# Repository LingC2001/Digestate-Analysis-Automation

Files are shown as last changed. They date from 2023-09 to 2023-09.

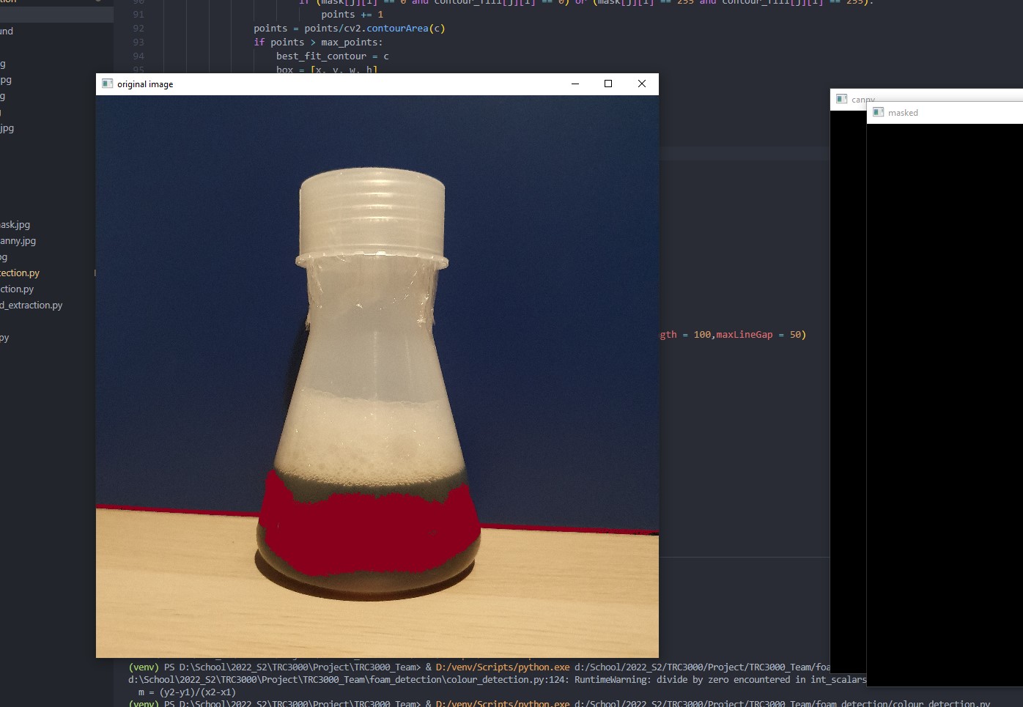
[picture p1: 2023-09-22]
foam_detection/images/noise_test.jpg

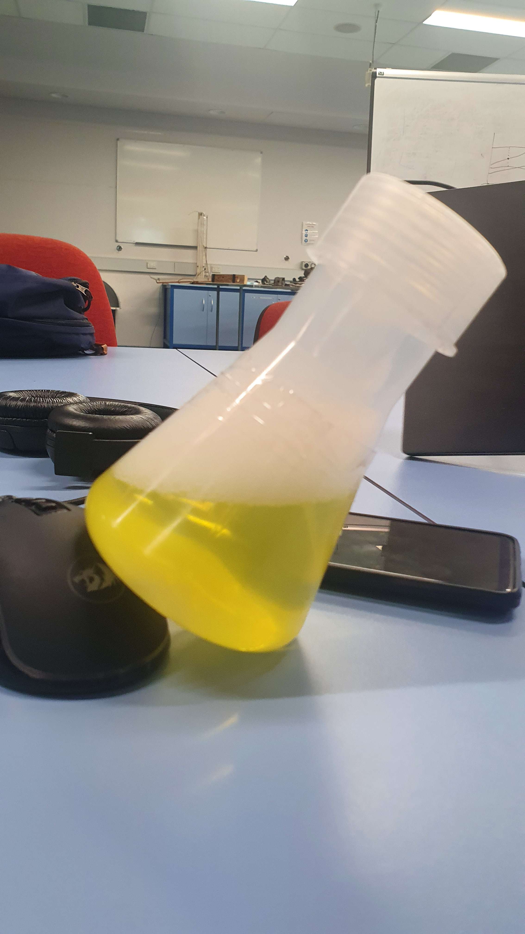
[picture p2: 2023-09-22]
foam_detection/images/test3.jpg

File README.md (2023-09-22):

# Digestate-Analysis-Automation
Development of an automated system for perfoming digestate analysis for anerobic tanks.

## Project Brief
In anaerobic digestion (AD), microorganisms are used to break down biodegradable material in the absence of oxygen. The process helps to solve two major problems in the world today. Firstly, it helps to to treat the biodegradable waste and sewage sludge that are produced in ever increasing amounts each year. Secondly, AD may be used as a source of renewable energy.
However, foaming poses an operational problem in anaerobic digesters. 

Project Objectives:
- Conduct operational interfacing of an anaerobic digester sample tester experimentation kit.
- Design a commercial ready portable anaerobic digester sample tester.

## Description
An machine learning approach was taken. Sample tester contains cameras, servos, load cells and temperature sensors to perform full analysis of digestate.

Design
Device
Foam Detection

### Built With
- 
- 
- 

## Authors
- Ling Chen, LingC2001@gmail.com | lche0147@student.monash.edu
- John Nguyen
- Xavier Andueza
- Kabir Chugh
- Jason Ltg
- Ritchie Leong

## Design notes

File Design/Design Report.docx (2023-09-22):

# Team232 Project Design

Part A: Supplementary information document

Xavier Andueza,

Ritchie Leong,

Ling Chen,

Kabir Chugh,

Jason Ung,

John,

# Executive Summary

Do after everything else has been written up.

Contents

1.0 Executive Summary 2

Contents 3

2.0 Introduction 4

3.0 Proof of Concept 5

3.1 Foam Detection Algorithm Summary 5

3.1.1 Background Removal 5

3.1.2 Bounding Box 5

3.1.3 Foam Detection Network 5

3.1.4 Information Extraction 5

4.0 Final Product Design 5

4.1 Expected End-Use Environment 5

4.2 Design Requirements 6

4.2.1 Hard Design Requirements 6

4.2.2 Soft Design Requirements 6

4.3 Overview of Final Product Design 7

4.4 Sub-assembly Analysis 7

5.0 Costings 7

# Introduction

Team 232’s innovative design is to be used for testing and diagnosis of digestate from an anaerobic digester (AD). It is intended to be portable, and carried around so that it can be screwed digestate release valves at customer sites.

The design is broken into three main sub-assemblies (SAs), being the:

- Hard plastic chassis, handle and rubber grip;
- Digestate container; and
- Electricals.

In creating the design, Team 232 has considered several hard and soft design requirements. The ways in which the requirements are met by the design are explored in this supplementary report. A part and purchase part list, with anticipated costs, notes and remarks are also included.

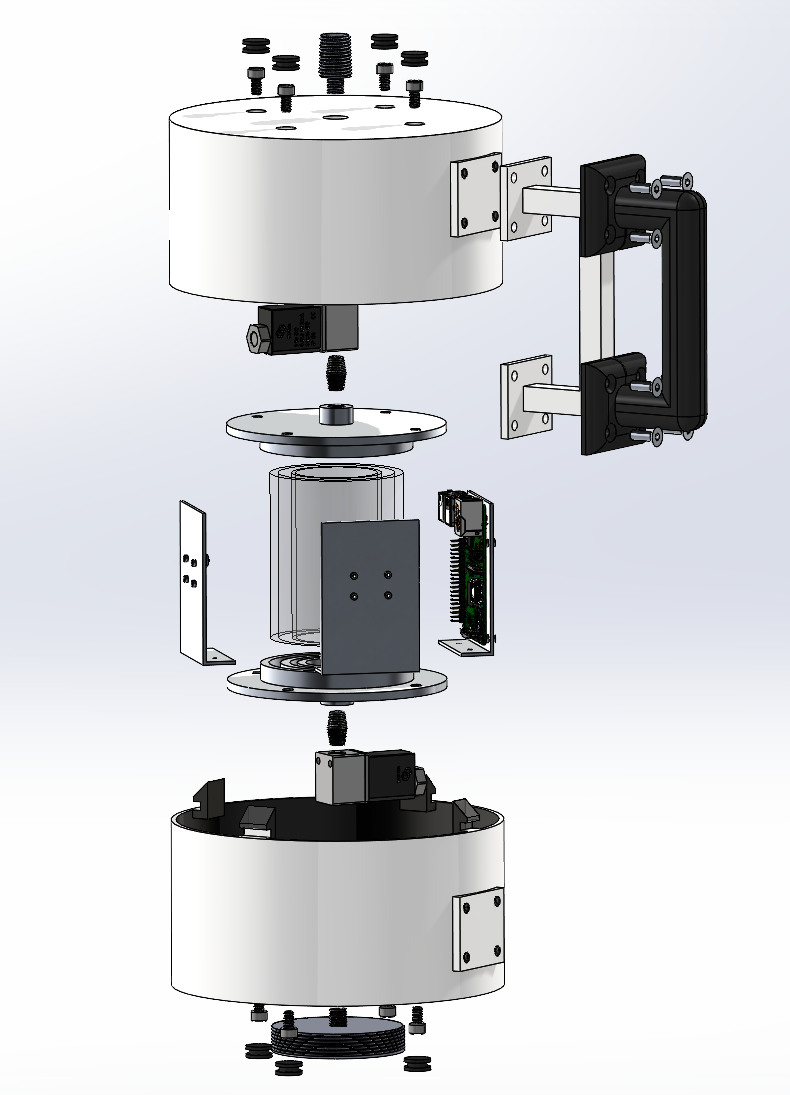
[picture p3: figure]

Figure 4.3.1: Expanded Mechanical Components View

# List of Design Requirements

All requirements were procured through market research performed by Monash University.

## Hard Requirements

The “Hard Requirements” are defined as the requirements that must be included in the design, and the design is considered insufficient without these.

Requirement | Specification
Hold digestate for analysis | ≥100mL
Dry weight (no digestate) | <10kg
Instrument base area | <0.08m^2
Hold electronics internally | -
Battery operated | -
Carry-friendly | -
No sharp corners | -

## Soft Requirements

The “Soft Requirements” can be considered to be the factors that are considered by the target audience when making a purchase decision, but are typically not deal breakers to them. Team 232 assigned weighting factors to the Soft Requirements to establish a hierarchy of importance. This enabled the team to make better decisions when maximising one factor may come at the expense of another.

Requirement | Aim | Weighting Factor
Cost | Minimise | 5
Weight | Minimise | 9
Height | Minimise, but ensure comfortable handling | 8
Surface Area | Minimise, but ensure comfortable handling | 8
Aesthetics | Aesthetically appealing | 3
Servicing Difficulty | Minimise | 5
Amount of metal parts | Minimise | 5
Manufacturing difficulty | Minimise | 5

# SA1: Hard Plastic Chassis, Handle and Rubber Grip Sub-Assembly

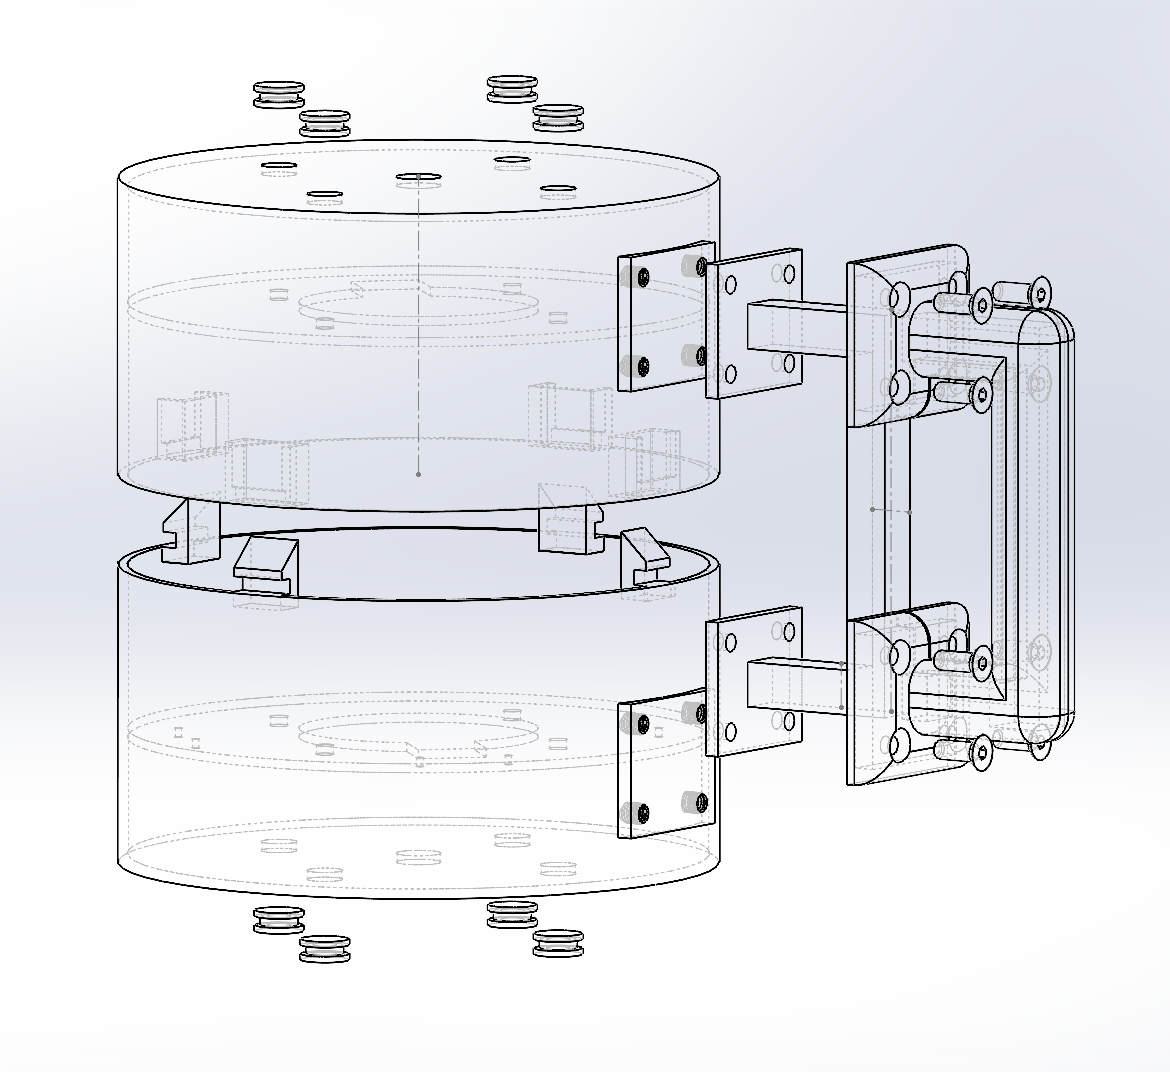
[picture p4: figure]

Figure X: AAA

## 4.1 Sub-Assembly Part List

Insert the part list

## 4.1 Hard Requirements Satisfied

Insert table and explanations

## 4.1 Soft Requirement Maximisation

Insert table and explanations

# SA2: Digestate Container

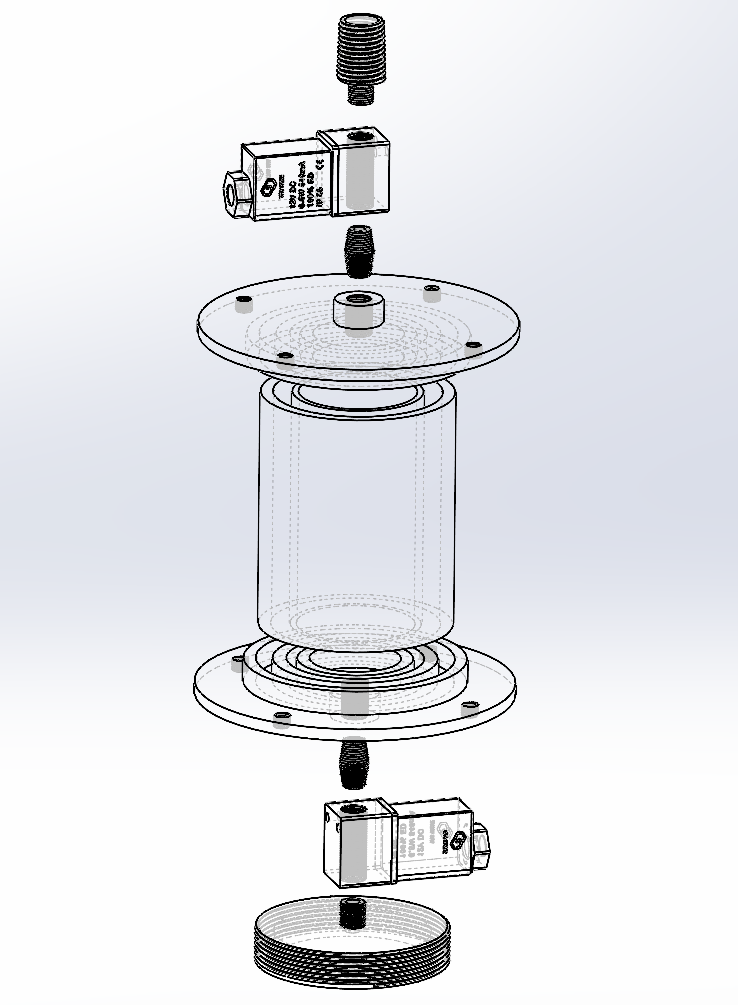
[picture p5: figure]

Figure X: AAA

## 4.1 Sub-Assembly Part List

Insert the part list

## 4.1 Hard Requirements Satisfied

Insert table and explanations

## 4.1 Soft Requirement Maximisation

Insert table and explanations

# SA3: Electricals

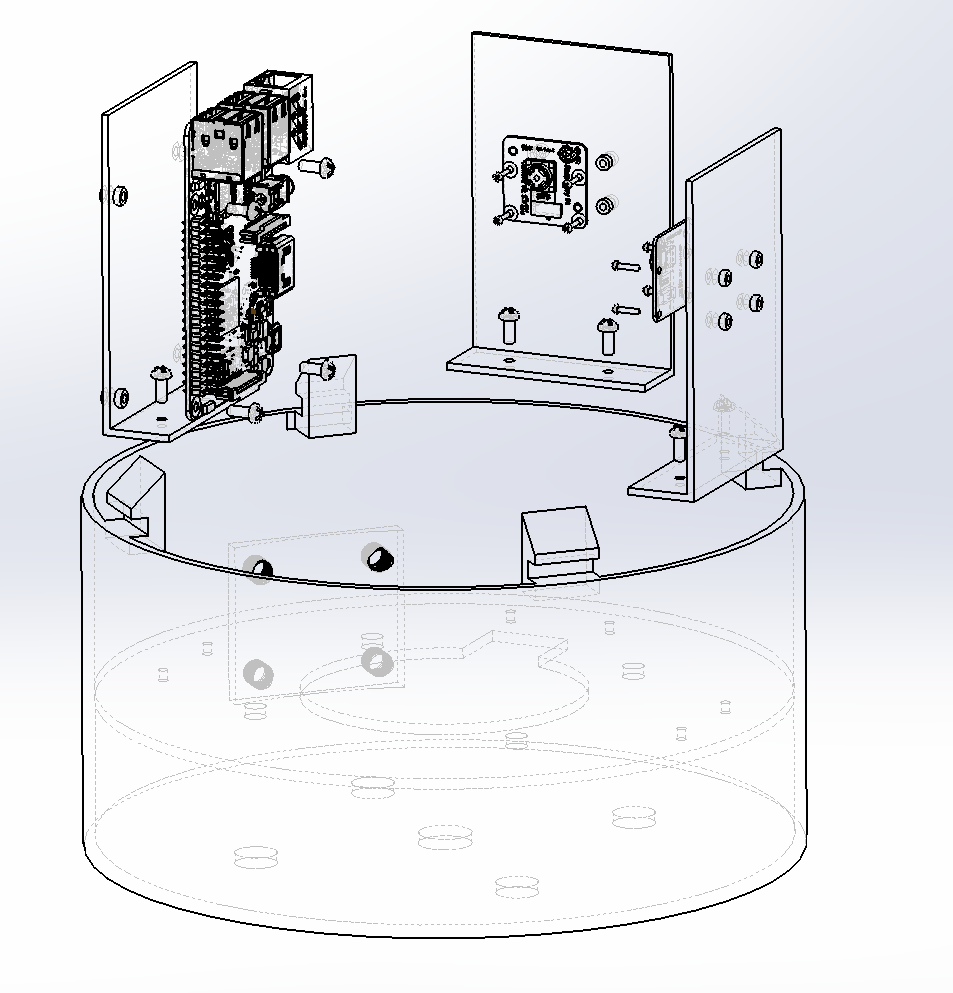
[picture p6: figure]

Figure X: AAA

## 4.1 Sub-Assembly Part List

Insert the part list

## 4.1 Hard Requirements Satisfied

Insert table and explanations

## 4.1 Soft Requirement Maximisation

Insert table and explanations

# 4.0 Final Product Design

## 4.1 Expected End-Use Environment

T232’s instrument's target audience is organisations that use ADs. These ADs will generally always be outside, and therefore the instrument will be exposed to a broad range of climates. The unit will be portable and will be taken closer to the ADs so that testing can be conducted. The unit may be transported and left in vehicles, which may expose the unit to even higher temperatures than the outside climate. Furthermore, T232’s Instrument may also experience significant shocks and vibrations at the customer sites, as users may accidentally drop the unit, or otherwise leave it unsecured in a vehicle as it travels bumpy roads. It is not anticipated that T232’s Instrument will be exposed to particularly detrimental electric shocks or electromagnetic interference.

Expected environments for the unit were defined as so:

Table 4.1: Expected end-use environmental conditions

Specification Type | Operational | Survival
Temperature | 0°C - 40°C | -20°C - 60°C
Humidity | 20-80% RH | 10-100% RH
Shock
Vibration

## 4.2 Design Requirements

Design requirements were established by engaging with the target audience and understanding their perspective, as well as an analysis of the conditions in the end-use environment. They were broken down into Hard Specifications (the “must-haves”) and Soft Specifications (which are maximised against).

### 4.2.1 Hard Design Requirements

Table 4.2.1: Hard Design Requirements

Requirement | Specification
Hold digestate for analysis | ≥100mL
Dry weight (no digestate) | <10kg
Instrument base area | <0.08m^2
Hold electronics internally | -
Battery operated | -
Carry-friendly | -
No sharp corners | -

### 4.2.2 Soft Design Requirements

Soft requirements were interpreted through a weighting factor. The higher the weighting factor the greater the design should factor this in.

Table 4.2.2: Soft Design Requirements

Requirement | Aim | Weighting Factor
Cost | Minimise | 5
Weight | Minimise | 9
Height | Minimise, but ensure comfortable handling | 8
Surface Area | Minimise, but ensure comfortable handling | 8
Aesthetics | Aesthetically appealing | 3
Servicing Difficulty | Minimise | 5
Amount of metal parts | Minimise | 5
Manufacturing difficulty | Minimise | 5

## 4.4 Sub-assembly Analysis

- Break things down into the individual sub-components. Explain the design decisions that were made, what they maximised and how assembly will work. Give details to dimensions:
  - Fluid compartment sub-assembly
    - Expanded assembly view
    - Details of components, how they would be manufactured
    - Details of joiner (Araldite Temperature Cured solution)
  - Outer shell
    - Expanded view
    - Highlight intended manufacturing method, plastic molds
    - Highlight clipping (and how it can only clip in the one way)
    - Highlight how grip is secured
  - Electronics
    - Image of electronics secured down
    - Highlight how, where they are secured

# 5.0 Costings

Provide reasonable costings breakdown

Table 5.1: Costing Summary

Parts | Quantity | Cost ($) per unit | Source

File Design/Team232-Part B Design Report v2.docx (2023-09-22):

# Part B Design Report Team232

Xavier Andueza,

Ritchie Leong,

Ling Chen,

Kabir Chugh,

Jason Ung,

John Nguyen

# 1. Design Features

## 1.1 Handle/Grip

One of the main features in our design is the handle. The handle allows the device to be carried around by the user. When held by the user, the handle is the most critical part supporting the weight of the whole device. Thus, we have analysed the handle by running FEA simulations to find the stresses and displacement of the handle.

# 2. Calculations and Assumptions

## 2.1 Mass of the device

### 2.1.1 Mass of components

- Tester device (derived from Solidworks) without the 10mm solenoid valve, Pi camera, Raspberry Pi 4, White LED strips, and battery is 2964.87g
- Two 10mm solenoid valve is 4.5g X 2 = 9g
- Two Pi camera is 3g X 2 = 6g
- Raspberry Pi is 46g
- 0.05m LED strips (3 LEDs) is 350g÷100=3.5g
- Battery is 57g

Total mass of the device is 2964.87g+9g++6g+46g+3.5g+57g=3086.37g

We analyse for the system at full volume of Anaerobic Digestate.

### 2.1.2 Size of the flask

The inner glass tube has an inner diameter 5cm (radius 2.5 cm) and height 10cm

The volume of the flask =πr^2 h=π×2.5^2 ×10=196.3cm^3

### 2.1.3 Mass of Anaerobic Digestate (AD)

The density of AD is approximately 1 g/cm^3

The maximum amount of AD allowed in the system is 196.3cm^3 ×1g/cm^3 =196.3g

## 2.2 Weight of the device

When the glass is fully filled with AD, the total weight of the device is

F_(Total) =((3086.37g+196.3g))/1000×(9.81m)/(s^2)=32.2N

## 2.3 Servomotor and Rotating platform

## 2.3.1 Turning speed of rotating platform

The servomotor rotates at a max operational speed and has a maximum range of 180°. To calculate the angular velocity in units of rad/s is as follows, where θ is how range of rotation in degrees, and t is time to reach said rotational angle in seconds.

Rotational speed ((rad)/s) = θ/t ×π/180

## 2.3.2 Angular control

From the gpiozero library, provided code details how the servomotor rotates. “servo.min()” rotates the servo to starting position or 0°. “servo.mid()” rotates to 90° or midway and “servo.max()” rotates to end position or 180°.

Another way to control the position of the servo is by setting the value of the servomotor using the line of code: “servo.value = x”, where x is a real number between –1(min) and 1(max). This implies that a value of –1 corresponds to 0°, 0 corresponds to 90° and 1 corresponds to 180°. From this a function was created whereby a user enters a value between 0° and 180°. θ is in angle of rotation in units of degrees.

Value = cos(θ) ×-1

However, because in Python, a math library is required to access these tools, the function is more accurately as follows:

servo.value = math.cos(math.radians(θ)) ×-1

# 3. Simulations

## 3.1 Handle/Grip

The weight (32.2N) of the device acting on the handle is used in the FEA simulation to find the stresses and displacement of the handle.

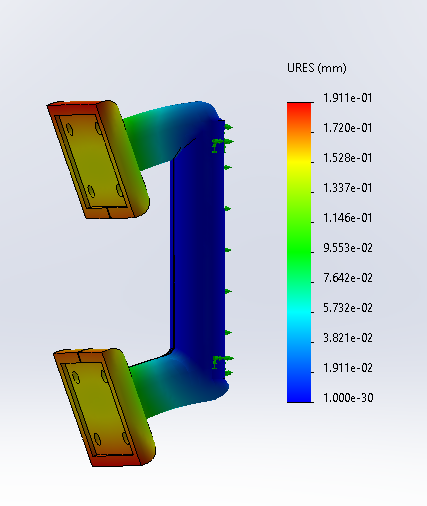
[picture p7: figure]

Figure 1: FEA displacement of handle and grip

Through FEA simulation, the max displacement of the handle (shown in Figure 1) is on the rubber grip. The max displacement is approximately 0.19mm, which is acceptable since the material is rubber. The max displacement on the plastic (ABS) handle itself is around 0.15mm and is negligible.

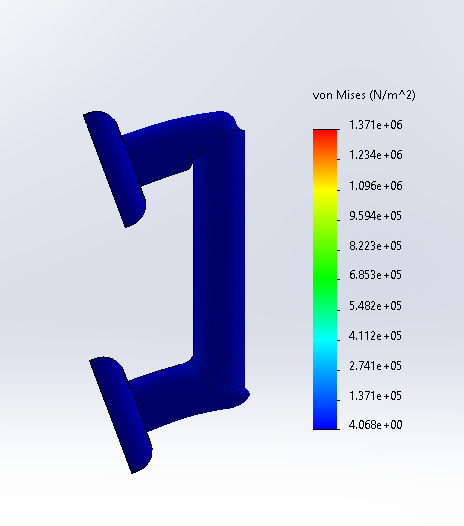
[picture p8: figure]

Figure 2: FEA stress of handle and grip

Through FEA simulation, the max stress (shown in Figure 2) experienced by the plastic handle is approximately 1.37MPa. The maximum allowed stress for ABS is 315MPa. So, the safety factor of the handle design is 230. Thus, we are very confident that the handle design will not fail, it is very safe.

# 4. Physical Experiments

## 4.1. Camera Testing

The proposed design of our device heavily relies on the reliability of the camera image analysis. It is the core functionality of the device and is crucial to the successful extraction of anerobic digestate information. The thorough tests in the following sub-sections are done to help determine and justify key design features needed to assist the functionality of the image analysis algorithm.

### 4.1.1. Background Removal Testing

Background removal is the first step needed in the analysis process; hence it is crucial to ensure successful background removal. The following Figure X

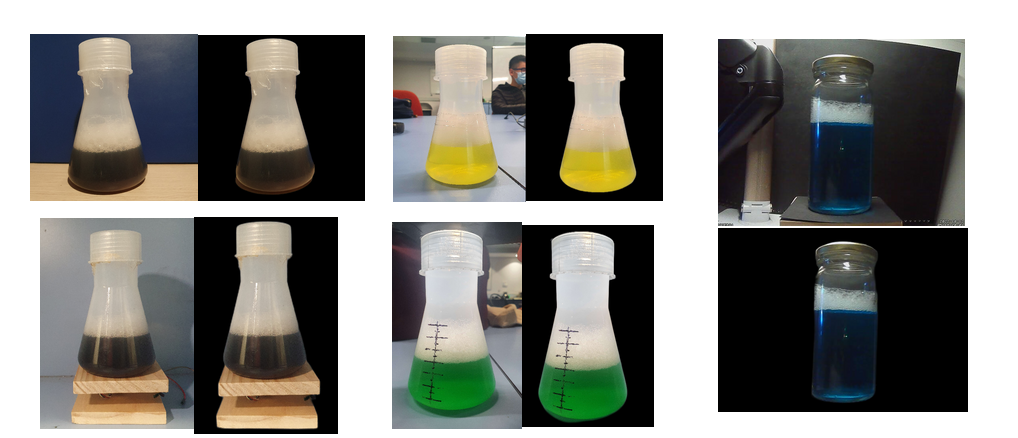
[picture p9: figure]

Figure 3:Background removal tests

As seen from Figure X, the background can be successfully removed in most environments, however there are still some cases where the useless and interfering objects remain in the image after removal. Therefore, to combat this problem in the design, we ensure that the glass tube containing the flask is completely sealed by an outer casing where the inside is painted black. This would completely remove the chance of unwanted background interference.

Furthermore, the background removal AI (Artificial Intelligence) is designed in a way where ideally the object of interest should be somewhere in the middle of the camera frame. In this design this is accounted for by keeping the anerobic digestate in a central glass tube and having the cameras pointed directly at it.

### 4.1.2. Image Resolution Testing

The image resolution test was done to determine the minimum required camera resolution that was needed to achieve accurate extraction of key information in the image. Using this information an appropriate camera suited for the purpose can be selected. Another small consideration was the running time of the code. The testing results are shown in Figure X below.

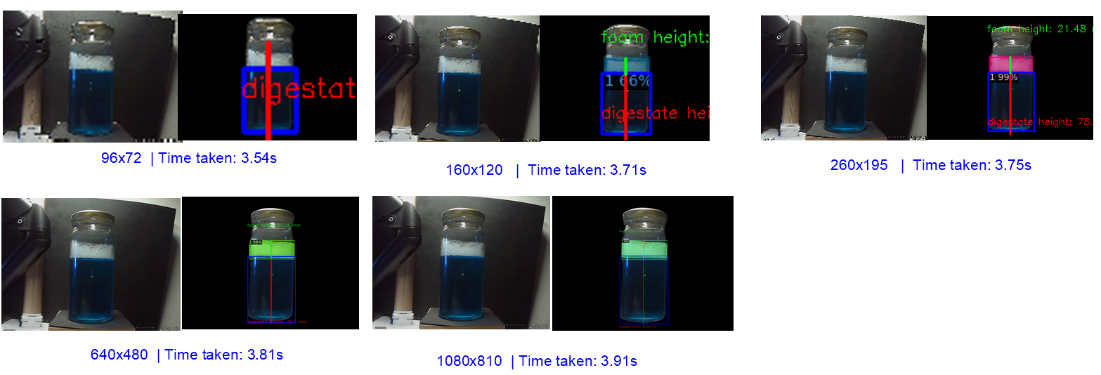
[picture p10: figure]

Figure 4:Camera resolution tests

Several conclusions can be drawn from the above Figure. Firstly, the tests demonstrate that foam and digestate regions can be accurately detected even with small resolution of 160x120, however it fails at resolutions below that due to too much loss of information. Another thing is that the lower the resolution, the more error the height measurements will be, as there are simply less pixels hence much larger height increments.

Another observation is that the running time of python scripts are similar despite the increase of resolution. This is due to the running time being primarily dominated by the loading of the neural network model weights. However, this test was done on a computer much more powerful than the raspberry pi, hence the actual running time may be longer.

Taking all of these into account, it was determined that 640x480 resolution is the best suited resolution that would reliably work with the algorithm without the loss of too much information. This also allows the design to be suited with a cheaper and lighter camera.

### 4.1.3. Algorithm Detection Robustness and Accuracy

To ensure that the detection algorithm is robust and accurate enough to use on digestate and foam of any colour and amount, thorough testing has been conducted on simulated samples of different colours and amounts. The figure below shows some tests done:

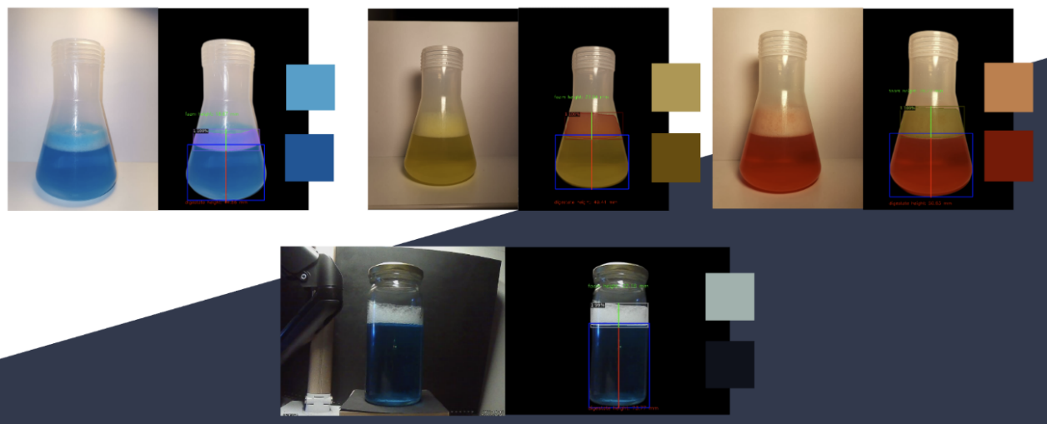
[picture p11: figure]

Figure 5: Varying Colour Tests

The results of these tests are summarised in the table below:

Table 1: Error Table

Test Sample | Detected Foam Height (mm) | Actual Foam Height (mm) | %Error | Detected Digestate Height (mm) | Actual Digestate Height (mm) | %Error
Light Blue | Less Foam | 19.31 | 17 | 13.59 | 42.26 | 42 | 0.62
Light Blue | More Foam | 25.61 | 25 | 2.44 | 48.92 | 46 | 6.35
Black | Less Foam | 20.39 | 19 | 7.32 | 44.12 | 43 | 2.60
Black| More Foam | 29.4 | 27 | 8.89 | 45.56 | 44 | 3.55
Green | Less Foam | 18.99 | 19 | 0.05 | 51.96 | 50 | 3.92
Green | More Foam | 28.92 | 29 | 0.28 | 50.06 | 48 | 4.29
Red | Less Foam | 19.23 | 17 | 13.12 | 48.44 | 46 | 5.30
Red | More Foam | 26.93 | 27 | 0.26 | 51.79 | 50 | 3.58
Yellow | Less Foam | 16.66 | 16 | 4.13 | 50.22 | 50 | 0.44
Yellow | More Foam | 26.32 | 26 | 1.23 | 50.25 | 50 | 0.50
Orange | Less Foam | 17.74 | 17 | 4.35 | 51.55 | 50 | 3.10
Orange | More Foam | 25.3 | 24 | 5.42 | 51.09 | 50 | 2.18
Average: | | | 5.09 % | | | 3.04%

As seen from the results above, the average error is around 3-5% which is acceptable for our design, however there were some images where error went as high as 13%. These cases of higher error are due to incorrect camera angles. When the camera angle is not directly perpendicular to the foam level line, it causes the side of the foam to appear taller in the camera than the centre of the foam, which causes errors in the foam bounding box detection. Another issue is the parallax error.

To minimise this, in the design the camera is placed directly facing the centre of the glass tube, and the amount of digestate in the device required for analysis will be consistent, hence the camera will always be pointed at the foam level, which helps to minimise the errors discussed above.

## 4.2 Servomotor Testing

## 4.2.1 Range of rotation

There exist many types of servomotors, which are characterized by their rotational behaviour. A continuous rotation servo is a servomotor that can rotate continuously in either direction for as long as the user desires. Speed of rotating and time rotating can be controlled. A linear servo is a servomotor that does not rotate but moves back and forth like a rack and pinon system. A positional rotation servo is a servomotor that is limited a range of roughly 180°. Only the position of the servo can be controlled. The positional rotation type servomotor was utilized in this project.

The gpiozero library was employed to allow rotational control of the servo. The minimum pulse width and maximum pulse width values are essential in determining the maximum range of rotation. Within the data sheet of servomotors contains the standard minimum and maximum pulse width values. However, as all servomotors are not built the same, these values are merely suggestions, and the true bounds of the range of rotation must be experimentally determined. It was found that at a minimum pulse width value of 0.5 milliseconds and a maximum pulse value of 2.33/1000 seconds satisfies the bounds of 180° rotation.

## 4.2.2 Varying speed and varying load

By varying the speeds and the load on the platform, we can identify patterns that could not have been clearly identified.

Modes of speed include - Slow, medium, fast and max speed.
Weight of loads include - No load, 100ml filled flask, 200ml filled flask and 300ml filled flask.

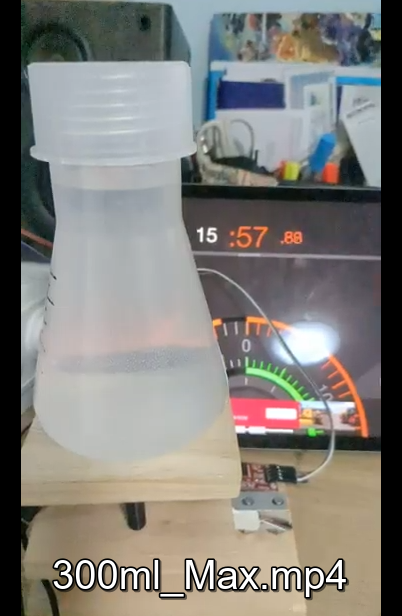
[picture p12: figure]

Figure 6: Flask with water on load cell

By placing a timer in the background, where its format includes milliseconds, we can use a x8 slow motion camera to measure the time taken to rotate to a specific angle. Through thorough testing and frame-by-frame analysis, we have obtained many samples and identified many relationships.

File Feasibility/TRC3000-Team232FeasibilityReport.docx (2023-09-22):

# Team232 Feasibility Report

Xavier Andueza,

Ritchie Leong,

Ling Chen,

Kabir Chugh,

Jason Ung,

John Nguyen

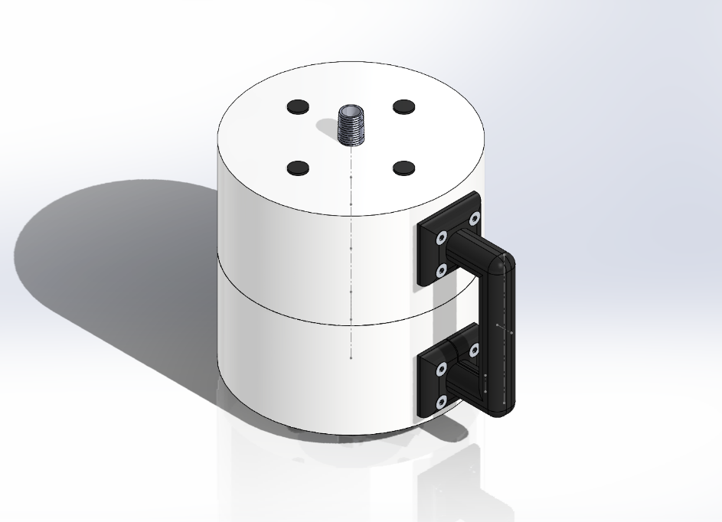
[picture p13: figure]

# 1.0 Executive Summary

Anaerobic Digestion (AD) in bioreactors can be significantly affected by the quality of the digestate contained within. Indicators of poor digestate quality include colour, and foaming. Testing of digestate quality is typically done by removing digestate from the container in an intermediate container, and then placing this digestate into a testing unit.

Team 232 (T232) has proposed an innovative new design that will disrupt this process, where the testing unit will plug directly into bioreactor release valves, immediately testing the digestate. In this feasibility report, the design is presented, and the three design sub-assemblies are justified, including estimated costs. Design decisions, including the material selection choices, are highlighted and explained. Visuals are presented to assist the reader in understanding how these sub-assemblies are assembled.

# 2 Introduction

In this report, the financial feasibility of the Team 232’s (T232’s) product is assessed. Justifications are made for the design decisions made, and costings are presented. References are made to the Bill of Material, which can be found accompanying this report.

## 2.1 Problem Statement

Anaerobic Digesters (AD) have been traditionally used in waste treatment to breakdown biodegradable waste and sewage sludge. It is also a source of renewable energy. However, the chemical processes can lead to a reduction in efficiency. This is indicated by foaming and a colour change in the digestate. Periodic testing of digestate must be performed, where the amount of foam and the foam colour is analysed. Intervention can occur if needed after analysing the digestate foam and colour.

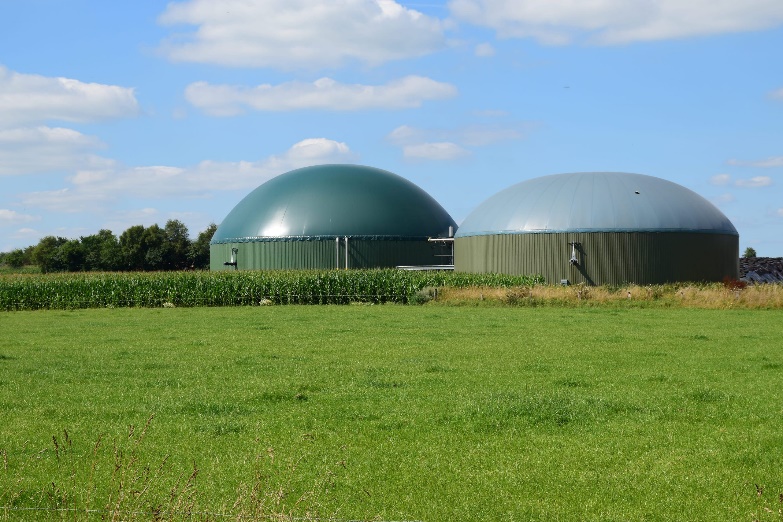
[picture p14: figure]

Figure 1: Anaerobic Digester plant

https://www.fgsorganics.co.uk/wp-content/uploads/2022/07/shutterstock_304576766-1-scaled.jpg

## 2.2 Proposed Solution

To enable better testing of ADs, Team 232 conducted successful proof-of-concept testing and has developed a proposed AD tester design, dubbed “T232’s Instrument”. T232’s Instrument enables rapid testing and diagnosis of digestate. The AD tester device allows users to extract a sample of the digestate from the AD tank and analyse digestate foam level and colour.

# 3 Design Summary

Figure 2: Image of the proposed final design of T232’s Instrument

T232’s Instrument can be broken down into three main sub-assemblies:

- The Chassis The hard plastic outer container that features the grip and contains the Fluid Compartment and Electronics within.
- The Digestate Container The metal and glass that contains the digestate during testing.
- The Electronics The circuits and other electrical components that enable analysis and diagnosis within the instrument.

These Sub-assemblies are broken down in their own segments, costings discussed, and design decisions justified.

## The Intention of the Design

To frame the design decisions made, the overall intended use of T232’s instrument will be explained.

Unlike other competitor products, where the digestate is brought to the instrument, T232’s is unique in that the instrument is brought to the unit. This is enabled through the design being such that the instrument is screwed into bioreactor fluid release valves. The digestate can then enter the body and be tested immediately.

# 4 The Chassis

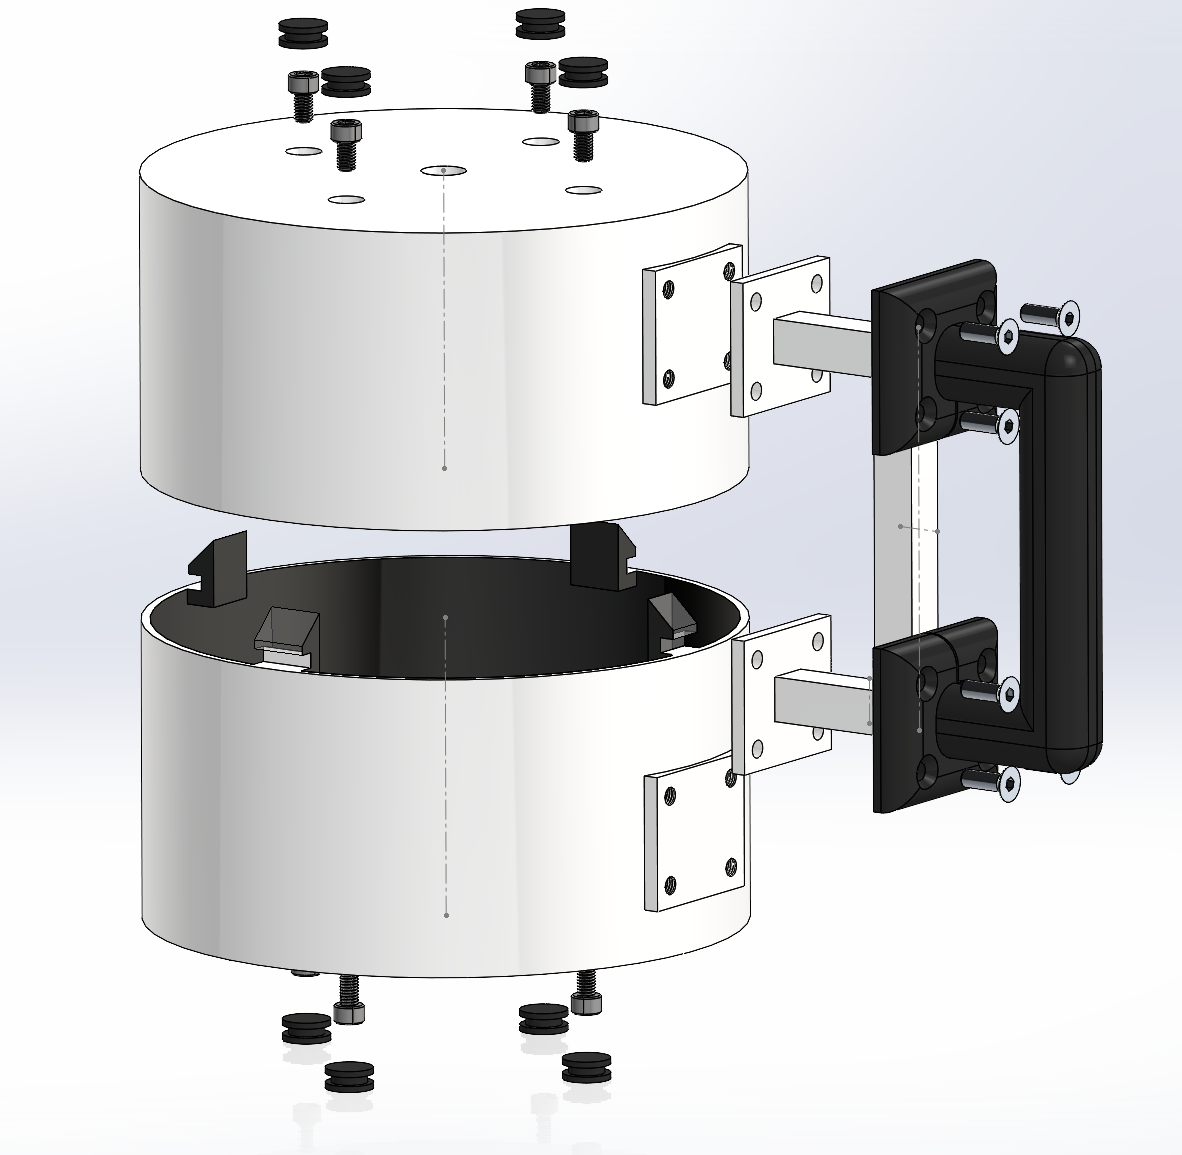
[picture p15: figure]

Figure 3: Disassembled view of T232’s Instrument’s Chassis

Table 1: Design justifications for the chassis

Name | Material | Cost ($) | Qty | Justification

Top Shell

Hard Plastic

58.55

x1

The top shell was decided to be made using a hard plastic, that is injection moulded. Hard plastic was deemed to be the most appropriate as it was a high priority for the design to be lightweight, but sturdy. Making the entire instrument out of Aluminium was considered, however it was deemed as being both too costly and heavy compared to the hard plastic.

The Top shell features four clip holes, which the bottom shell clips into for easy assembly. One of the clips is smaller than the others, meaning that there is only one way to assemble these two together, as it will not fit in any other way. This ensures that the handle holes in the top shell are aligned. It is a simple method that ensures that the manufacturing process is simple, yet able to ensure fewer mistakes are made.

Both the top and bottom shell feature holes for the 10mm M6 HEX heads to pass through, securing the Digestate Compartment to the Chassis. To enable the large solenoids to enter the bottom sections, there is a large opening for them.

Both the top and bottom shell have their inside painted black so that the images easily have the foam and background distinguished.
Bottom Shell | Hard Plastic | 58.51 | x1 | The Bottom shell features the bottom clips, that clip into the top shell clip shells.
10mm M6 HEX Bolt | Steel | 4.96 | x8 | These 10mm M6 HEX screws were chosen as they allow a large amount of torque to be applied. These secure the Digestate Compartment to the chassis. The top and bottom shell have holes, which allow the bolts to be screwed in through. HEX heads have an advantage of being resistant to threading, which, due to large torques being applied to ensure that the chassis and the fluid compartment, is a risk for other heads.
Rubber Nibs | Rubber | 8.00 | x8 | The rubber caps are placed onto the screw holes that exist in the chassis, and were chosen as rubber material is already being used on the grip, and to strengthen the black-on-white aesthetic of the instrument.
Handle | Hard Plastic | 21.38 | x1 | The handle is made of hard plastic, which is strong yet lightweight. As a rubber grip is placed on top of this, costs were reduced by making the grip square. This part is simple to injection mould, and will be quite cheap. Metals would be more expensive and weigh more.
Grip | Rubber | 33.87 | x1 | The Grip was selected to be a custom rubber grip, which is screwed into the handle and chassis through the 18mm countersunk M6 HEX Screws. Rubber grips are commonplace, and are comfortable to many consumers. A softer rubber allowed the handle design to be simpler, further reducing costs.
18mm countersunk M6 HEX Bolt | Steel | 8.70 | x8 | These 18mm countersunk M6 HEX screws are used to secure the grip and handle together, and into the chassis. These are utilised in place of the 10mm M6 HEX due to their need to be countersunk and the overall hole length being greater. Countersunk screws were chosen as these screws were customer facing, and having bulkier HEX heads resulted in a significantly loss of visual appeal to the customer, as screws were jutting out from the grip, which most customers associate with being smooth.

# 5 The Fluid Container

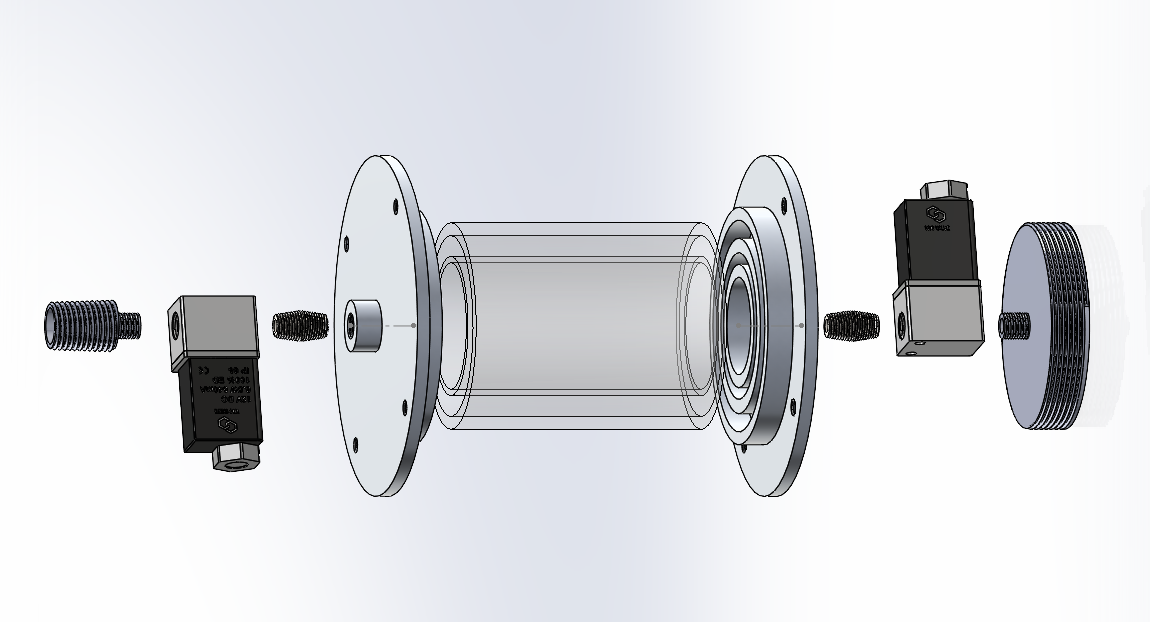
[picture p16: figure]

Figure 4: Disassembled view of the Digestate Container (flipped horizontally)

Table 2: Design justifications for the Digestate Container

Name | Material | Cost ($) | Qty | Justification
Valve connector | Stainless Steel Alloy | 66.00 | 1 | This valve connector was initially designed as a 20mm NPT head; however, it is extremely customisable to customer site needs. It was not worthwhile investigating off-the-shelf components due to the likely amount of variation from one customer site to another. A stainless-steel alloy was chosen for this part as the digestate, although anaerobic, may induce some rusting effects over time as air enters when outside of testing environments.
10mm 24V DC Solenoid Valve | NA | 99.00 | 2 | The solenoid valves are crucial to the intended purpose of the system. These valves control the flows in and out of the instrument and are highly precise. The valves are controlled via feedback from the raspberry Pi and will fill the glass vial up to the measurement point. These specific valves were chosen due to their smaller size, and appropriate valve opening widths.
Male-to-Male 10mm NPT connector | Stainless Steel Alloy | 98.00 | 2 | An NPT male-to-male connector was used as it ensures that there is extremely low chance of leakage, and also is a very simple way of connecting the solenoid valves to the tube plates.
Tube plates | Aluminium Alloy | 165.00 | 2 | The tube plates are custom made, and feature two sections for the glass tubes to be inserted into. Glass tubes are secured to the plates with adhesive. An aluminium alloy was selected due to the thicker nature of these components, and how the mass would make the unit less transportable and place greater strain on the glass tubes. The part is as thick as it is as this is where the digestate container is secured to the chassis with the 10mm M6 HEX bolts.

54mm wide, 2.5mm thick, 100mm tall tube

Glass

32.24

1

Glass was chosen as it is inert and allows for light to pass through for measurement purposes.

The dimensions of this were chosen as it enabled the digestate container to hold 100ml of fluid halfway up the glass vial, which was deemed the optimal camera location. The glass thickness was selected as this was the most representative of world-proven double-glazed glass.

This is also standard glass tubing that can be easily and cheaply ordered from many suppliers.

By providing insulation in this manner, the unit does not require heating elements to keep the digestate in its mesophilic state during testing. This significantly reduces design complexity and costs.
80mm wide, 5mm thick, 100mm tall tube | Glass | 3.95 | 1 | These dimensions were chosen as they enabled the standard double-glazed glass air gap between the two glass tubes. They are also slightly thicker than the standard outer-glass size, ensuring extra robustness from shocks and vibrations. This is also standard glass tubing that can be easily and cheaply ordered from many suppliers.
Bottom attachment | Aluminium Alloy | 54.00 | 1 | The aluminium alloy was selected as this is also one of the thickest parts and adds significant weight to the build. Stainless steel was deemed too heavy. This is a custom part and will be constant across all builds.

# 6 The Electronics

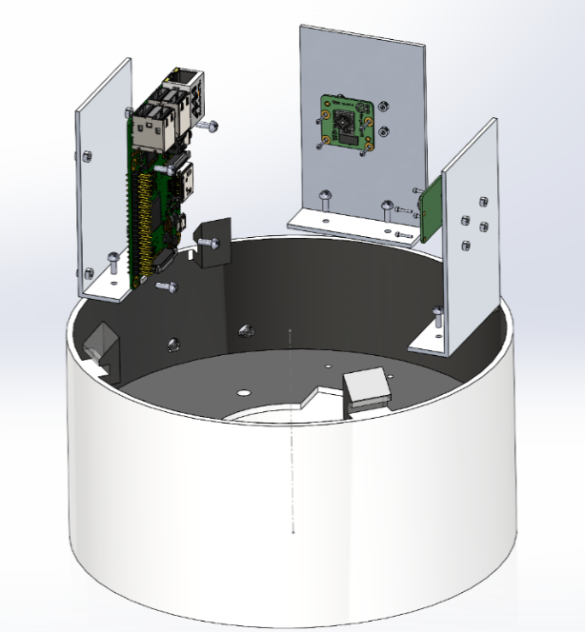
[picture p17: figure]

Figure 5: Disassembled Electronic Assembly

## 6.1 Raspberry Pi

The main computer for the device is the Raspberry Pi 4 Model B (Pi 4B), which has the sufficient random-access memory (RAM) of 4GB required to perform the live streaming and processing of the image taken. It is also relatively compact, lightweight, and affordable. Apart from the supply chain issues that prevent the scaling of manufacturing, the Pi 4B has a large community of users, which offers easily accessible help and support needed during development. The Pi 4B also comes with a variety of Linux based operating systems, which does not come with firmware development limitations from MacOS and Windows. The Pi Camera integrates well with the Pi 4B, which limits undetectable hardware malfunctions during later periods of the product life cycle. The Pi also has a typical 5.1V intake power, which can be provided with smaller battery and charging circuit packages. The GPIO pins on the Pi allows for affordable control of peripherals without investment into pricey Data Acquisition boards (DAQ).

## 6.2 Battery

The Pi Idle power consumption is measured using the prototype to be of 500mA, with the maximum peripheral consumption of 1000mA when the servo is activated (unrestricted). Since the operation of the servo is infrequent, the general power for the consumption is assumed to be of 600mA. With the inclusion of the PiJuiceHAT, we have 1820 mAh off the shelf Lipo, and additional 10000mAh PiJuice power pack equates to a total of 11820 mAh. The usage of the battery packs reduces weight, and space compared to cylindrical LiPo batteries. The PiJuiceHAT has inbuilt interruptible power supply, which is needed for a reliable product. The pi will not function predictably with slightly low/ high voltage fluctuations.

With an average consumption of 600mA, the device will last up to 19.2 hours per full charge.

## 6.3 Camera

The Pi Cam v2 has a max resolution of 1080p30 (1920x1080 progressive at 30 frames per second), which is sufficient for the 600x420 pixel photos that are needed for the foam height and digestate colour detection. Since the photo capture is instantaneous, the frames per second capacity is not a constraint.

## 6.4 Peripherals

Table 3: Electrical Peripherals Design Justifications

Name | Total Cost ($) | Qty | Justification
White LED strips | 0.26 | 50mm | Any generic White LEDs can be used.
Load Cell and Amplifier | 24.4 | x1 | HX711 is used to amplify the voltages in the 1kg bending load cells used
Solenoid Valves | 28.48 | x2 | These are low cost 5V solenoids that can take power from the Pi
Camera, LED holder | 193.00 | x2 | Plate to mount Pi cameras onto
Pi holder | 120.00 | x1 | Plate to mount the Raspberry Pi onto
Pi Camera | 106.82 | x2 | Core components
Raspberry Pi 4B/4GB | 88.09 | x1 | Core component

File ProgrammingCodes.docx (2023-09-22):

# Servomotor

## servo.py

Author(s): Jason Ltg

from gpiozero import Servo

import math

from time import sleep

from gpiozero.pins.pigpio import PiGPIOFactory

factory = PiGPIOFactory()

servo = Servo(17, min_pulse_width = 0.5/1000, max_pulse_width = 2.33/1000, pin_factory=factory)

servo.min()

try:

while True:

#Ask user for angle and turn servo to it

try:

angle = float(input('Enter an angle between 0 & 180: '))

except ValueError:

print("No... Input is not a number")

continue

else:

if angle > 180:

print('Not so high, between 0 and 180 please!')

continue

elif angle < 0:

print('No negatives, between 0 and 180 please!')

continue

# print("Type of number ", type(angle))

servo.value = math.cos(math.radians(angle)) * -1

sleep(1)

except KeyboardInterrupt:

sleep(1)

servo.mid()

sleep(1)

#servo.stop() // These two lines are not functions of the library...

#GPIO.cleanup()

print("\nGoodbye!")

#while True:

# for i in range (0, 360):

# print(i)

# servo.value = math.sin(math.radians(i))

# sleep(0.01)

#while True:

# for i in range (0, 360,10):

# print(i)

# servo.value = math.sin(math.radians(i))

# sleep(0.1)

#servo.min()

#sleep(1)

#servo.mid()

#sleep(1)

#servo.max()

#sleep(1)

#servo.value = -1

#sleep(1)

#servo.value = 0

#sleep(1)

#servo.value = 1

#sleep(1)

# IMU

## MPU_Measure.py

Author(s): John Nguyen

import smbus #import SMBus module of I2C

from time import sleep #import

import math

import time

import cv2

#some MPU6050 Registers and their Address

PWR_MGMT_1 = 0x6B

SMPLRT_DIV = 0x19

CONFIG = 0x1A

GYRO_CONFIG = 0x1B

INT_ENABLE = 0x38

ACCEL_XOUT_H = 0x3B

ACCEL_YOUT_H = 0x3D

ACCEL_ZOUT_H = 0x3F

GYRO_XOUT_H = 0x43

GYRO_YOUT_H = 0x45

GYRO_ZOUT_H = 0x47

def MPU_Init():

#write to sample rate register

bus.write_byte_data(Device_Address, SMPLRT_DIV, 7)

#Write to power management register

bus.write_byte_data(Device_Address, PWR_MGMT_1, 1)

#Write to Configuration register

bus.write_byte_data(Device_Address, CONFIG, 0)

#Write to Gyro configuration register

bus.write_byte_data(Device_Address, GYRO_CONFIG, 24)

#Write to interrupt enable register

bus.write_byte_data(Device_Address, INT_ENABLE, 1)

def read_raw_data(addr):

#Accelero and Gyro value are 16-bit

high = bus.read_byte_data(Device_Address, addr)

low = bus.read_byte_data(Device_Address, addr+1)

#concatenate higher and lower value

value = ((high << 8) | low)

#to get signed value from mpu6050

if(value > 32768):

value = value - 65536

return value

bus = smbus.SMBus(1) # or bus = smbus.SMBus(0) for older version boards

Device_Address = 0x68 # MPU6050 device address

MPU_Init()

# print (" Reading Data of Gyroscope and Accelerometer")

def Average(l):

avg = sum(l) / len(l)

return avg

t = 0

angle_x = 0

angle_y = 0

angle_z = 0

pi = math.pi

avg_Ax = [0]*20

avg_Ay = [0]*20

avg_single_Ax = 0

avg_single_Ay = 0

Vx = 0

Vy = 0

Vz = 0

prev_time = time.time()

Ax_max = 0

Ay_max = 0

Az_max = 0

while cv2.waitKey(100) != "q":

# for i in range(20):

#Read Accelerometer raw value

acc_x = read_raw_data(ACCEL_XOUT_H)

acc_y = read_raw_data(ACCEL_YOUT_H)

acc_z = read_raw_data(ACCEL_ZOUT_H)

#Read Gyroscope raw value

gyro_x = read_raw_data(GYRO_XOUT_H)

gyro_y = read_raw_data(GYRO_YOUT_H)

gyro_z = read_raw_data(GYRO_ZOUT_H)

#Full scale range +/- 250 degree/C as per sensitivity scale factor

Ax = -0.02 + acc_x/16384.0

Ay = -0.07 + acc_y/16384.0

Az = 1.06 + acc_z/16384.0

if abs(Ax) > abs(Ax_max):

Ax_max = Ax

if abs(Ay) > abs(Ay_max):

Ay_max = Ay

if abs(Az) > abs(Az_max):

Az_max = Az

Gx = 0.56 + gyro_x/131.0

Gy = 0.19 + gyro_y/131.0

Gz = -0.19 + gyro_z/131.0

#avg_Ax[i] = Ax

#avg_Ay[i] = Ay

#avg_single_Ax = Average(avg_Ax);

#avg_single_Ay = Average(avg_Ay);

#angle_x = round(avg_single_Ax * 90, 4) # @90d Ax = 1... 1*x=90, x=90

#angle_y = round(avg_single_Ay * 91.4, 4) # @90d Ay=0.985... 0.985*y=90, y=91.4

dt = time.time()-prev_time

prev_time = time.time()

# if abs(Ax) <0.05:

# Ax = 0

# if abs(Ay) <0.05:

# Ay = 0

# if abs(Ay) <0.05:

# Ay = 0

Vx += Ax *dt

Vy += Ay *dt

Vz += Az *dt

# print ("Gx=%.2f" %Gx, u'\u00b0'+ "/s", "\tGy=%.2f" %Gy, u'\u00b0'+ "/s", "\tGz=%.2f" %Gz, u'\u00b0'+ "/s", "\tAx=%.2f g" %Ax, "\tAy=%.2f g" %Ay, "\tAz=%.2f g" %Az)

#sleep(0.1)

# print ("\tTime=%.2f s" %t)

# print("acc_x:", Ax, "acc_y:", Ay, "acc_z:", Az)

# Sprint("angle_x:", angle_x, "angle_y:", angle_y)

#print(str(round(angle_y)))

#print(str(round(angle_x)))

print ("Current Gx=%.2f" %Gx, "\tCurrent Gy=%.2f" %Gy,"\tCurrent Gz=%.2f" %Gz)

#print("avg_Ax=%.2f" %avg_single_Ax, "avg_Ay=%.2f" %avg_single_Ay)

#print ("angle_x=%.2f" %angle_x, "\tangle_y=%.2f" %angle_y)

print ("Current Ax=%.2f" %Ax, "\tCurrent Ay=%.2f" %Ay,"\tCurrent Az=%.2f" %Az)

print ("Max Ax=%.2f" %Ax_max, "\t\tMax Ay=%.2f" %Ay_max,"\t\tMax Az=%.2f" %Az_max)

# print("Vx=%.2f" %Vx, "\tVy=%.2f" %Vy,"\tVz=%.2f" %Vz)

# print ("gyro_x=%.2f" %gyro_x, "\tgyro_y=%.2f" %gyro_y,"\tgyro_z=%.2f" %gyro_z)

# print ("acc_x=%.2f" %acc_x, "\tacc_y=%.2f" %acc_y,"\tacc_z=%.2f" %Gz)

# Load Cell

## load_cell.py

Author(s): John Nguyen

#! /usr/bin/python2

import time

import sys

import RPi.GPIO as GPIO # Import Raspberry Pi GPIO library

EMULATE_HX711=False

referenceUnit = 201

offset = 5

if not EMULATE_HX711:

import RPi.GPIO as GPIO

from hx711 import HX711

else:

from emulated_hx711 import HX711

def cleanAndExit():

print("Cleaning...")

if not EMULATE_HX711:

GPIO.cleanup()

print("Bye!")

sys.exit()

def button_callback(channel):

offset = val

print('offset when tare =',round(offset,3))

print("Tare done! Add weight now...")

hx.reset()

hx.tare()

time.sleep(1)

GPIO.setwarnings(False) # Ignore warning for now

GPIO.setmode(GPIO.BCM) # Use physical pin numbering

GPIO.setup(16, GPIO.IN, pull_up_down=GPIO.PUD_DOWN) # Set pin 10 to be an input pin and set initial value to be pulled low (off)

GPIO.add_event_detect(16,GPIO.RISING,callback=button_callback) # Setup event on pin 10 rising edge

hx = HX711(5, 6)

# I've found out that, for some reason, the order of the bytes is not always the same between versions of python, numpy and the hx711 itself.

# Still need to figure out why does it change.

# If you're experiencing super random values, change these values to MSB or LSB until to get more stable values.

# There is some code below to debug and log the order of the bits and the bytes.

# The first parameter is the order in which the bytes are used to build the "long" value.

# The second paramter is the order of the bits inside each byte.

# According to the HX711 Datasheet, the second parameter is MSB so you shouldn't need to modify it.

hx.set_reading_format("MSB", "MSB")

# HOW TO CALCULATE THE REFFERENCE UNIT

# To set the reference unit to 1. Put 1kg on your sensor or anything you have and know exactly how much it weights.

# In this case, 92 is 1 gram because, with 1 as a reference unit I got numbers near 0 without any weight

# and I got numbers around 184000 when I added 2kg. So, according to the rule of thirds:

# If 2000 grams is 184000 then 1000 grams is 184000 / 2000 = 92.

#hx.set_reference_unit(113)

hx.set_reference_unit(referenceUnit)

hx.reset()

hx.tare()

# print("Tare done! Add weight now...")

# to use both channels, you'll need to tare them both

#hx.tare_A()

#hx.tare_B()

while True:

try:

# These three lines are usefull to debug wether to use MSB or LSB in the reading formats

# for the first parameter of "hx.set_reading_format("LSB", "MSB")".

# Comment the two lines "val = hx.get_weight(5)" and "print val" and uncomment these three lines to see what it prints.

# np_arr8_string = hx.get_np_arr8_string()

# binary_string = hx.get_binary_string()

# print binary_string + " " + np_arr8_string

# Prints the weight. Comment if you're debbuging the MSB and LSB issue.

val = hx.get_weight(5)

#if GPIO.input(16) == 1 and val<2000:

# offset = val

if val > 2000:

val = 0

print(str(round(val,3)))

# Open a file with access mode 'a'

file_object = open('weights.txt', 'a')

# Append 'hello' at the end of file

file_object.write(str(round(val,3))+"\n")

# Close the file

file_object.close()

# To get weight from both channels (if you have load cells hooked up

# to both channel A and B), do something like this

#val_A = hx.get_weight_A(5)

#val_B = hx.get_weight_B(5)

#print "A: %s B: %s" % ( val_A, val_B )

hx.power_down()

hx.power_up()

time.sleep(0.01)

except (KeyboardInterrupt, SystemExit):

cleanAndExit()

# Camera

## usb_camera.py

Author(s): Ling Chen

import cv2

camera = cv2.VideoCapture(0)

# print(camera.isOpened())

ret, image = camera.read()

cv2.imwrite("foam_img.jpg", image)

camera.release()

del(camera)

## pi_camera_image.py

Author(s): Ritchie Leong

from picamera import PiCamera

import time

camera = PiCamera()

camera.resolution = (640, 960) #set resolution

camera.vflip = False #set the camera upright

# camera.start_preview() #camera display on the screen

time.sleep(2) #sleep 5 seconds

#take photo after running the code for 2 seconds

camera.capture("foam_img.png")

#image taken is saved as jpg file in the same directory. Saved on desktop in this case

camera.close()

# time.sleep(1) #sleep 1 seconds

# camera.stop_preview() #close camera display on the screen

## pi_camera_video.py

Author(s): Ritchie Leong

from picamera import PiCamera

import time

camera = PiCamera()

#set camera resolution

camera.resolution = (640, 360)

#set camera position upright

camera.vflip = True

#turn on camera after 5 seconds when code runs

camera.start_preview()

time.sleep(5)

#start recording and stop after 3 seconds

camera.start_recording("videotest.h264") #video is saved as .h264 file

time.sleep(3)

camera.stop_recording()

time.sleep(2) #sleep 2 seconds

camera.stop_preview() #close camera display on the screen

# Image Analysis

## process_img.py

Author(s): Ling Chen

import numpy as np

import sys

sys.path.append("foam_detection/")

sys.path.append("foam_detection/detectron2-main/")

sys.path.append("detectron2-main/")

sys.path.append("foam_detection/rembg-main/")

from utils.rescaleFrame import rescaleFrame

from utils.getEdges import getEdges

from utils.getDigestateInfo import getDigestateInfo

from utils.toBinary import toBinary

from utils.getBoundingBox import getBoundingBox

from utils.getFoamFromModel import getFoamFromModel

from utils.colourBlockDetection import colourBlockDetection

import rembg

import cv2

def process_img(image=None):

# image = cv2.imread("foam_detection/images/clear.jpg")

# image = cv2.imread("foam_detection/images/fg1.jpg")

if image is None:

image = cv2.imread("foam_detection/foaming_images/test2.jpg")

# image = cv2.imread("foam_detection/foaming_images/Yellowx3_foamx5.jpg")

scale = 720/max(image.shape[0],image.shape[1])

image = rescaleFrame(image, scale)

# cv2.imshow("original_image", image)

# Removing the backgorund using AI method from rembg package

flask_img = rembg.remove(image)

flask_img = cv2.cvtColor(flask_img, cv2.COLOR_BGRA2BGR)

# # Optional: Remove Glare

# flask_img = removeGlare(flask_img, 210)

cv2.imshow("removed_background", flask_img)

# foam - foam height - digestate - digestate height

viz0000 = flask_img.copy()

viz0001 = flask_img.copy()

viz0010 = flask_img.copy()

viz0011 = flask_img.copy()

viz0100 = flask_img.copy()

viz0101 = flask_img.copy()

viz0110 = flask_img.copy()

viz0111 = flask_img.copy()

viz1000 = flask_img.copy()

viz1001 = flask_img.copy()

viz1010 = flask_img.copy()

viz1011 = flask_img.copy()

viz1100 = flask_img.copy()

viz1101 = flask_img.copy()

viz1110 = flask_img.copy()

viz1111 = flask_img.copy()

viz_list = [viz0000, viz0001, viz0010, viz0011, viz0100, viz0101, viz0110, viz0111, viz1000, viz1001, viz1010, viz1011, viz1100, viz1101, viz1110, viz1111]

viz_list_str = ["viz0000", "viz0001", "viz0010", "viz0011", "viz0100", "viz0101", "viz0110", "viz0111", "viz1000", "viz1001", "viz1010", "viz1011", "viz1100", "viz1101", "viz1110", "viz1111"]

# Get the bounding box of the flask

box = getBoundingBox(flask_img)

x, y, w, h = box

# Get bounding box of the foam using trained mask rcnn model

no_foam = False

n = 0

for i in range(len(viz_list)):

if viz_list_str[i][-4] == "1":

if n == 0:

n+=1

foam_bbox, viz_list[i] = getFoamFromModel(viz_list[i])

foam_viz = viz_list[i].copy()

else:

viz_list[i] = foam_viz.copy()

if foam_bbox == None:

no_foam = True

else:

foam_edge = round(max(foam_bbox[3], foam_bbox[1]))

# cv2.imshow("foam_viz", viz_list[-1])

# Extract important digestate info from image and canny edges

digestate_info = getDigestateInfo(flask_img, box, foam_bbox, no_foam)

liquid_colour = digestate_info["digestate colour"]

liquid_height = digestate_info["digestate height"]

true_liquid_height = digestate_info["real digestate height"]

if not no_foam:

foam_height = digestate_info["foam height"]

foam_colour = digestate_info["foam colour"]

true_foam_height = digestate_info["real foam height"]

# Get bounding box of colours

for i in range(len(viz_list)):

if viz_list_str[i][-2] == "1":

viz_list[i] = colourBlockDetection(flask_img, viz_list[i], liquid_colour)

# Displaying the detected colour

colour = np.zeros((100,100,3), dtype = "uint8")

for i in range(100):

for j in range(100):

colour[i][j] = liquid_colour

# cv2.imshow("colour_of_liquid", colour)

# Displaying the detected foam colour

if not no_foam:

colour_foam = np.zeros((100,100,3), dtype = "uint8")

for i in range(100):

for j in range(100):

colour_foam[i][j] = foam_colour

# cv2.imshow("colour_of_foam", colour_foam)

# Displaying height lines

if no_foam:

for i in range(len(viz_list)):

if viz_list_str[i][-1] == "1":

# Displaying the detected digestate/liquid height

cv2.line(viz_list[i], (x+(w//2), y+h-(liquid_height)), (x+(w//2),y+h), (0, 0, 255), 2)

string = "digestate height: " + str(round(true_liquid_height*1000,2)) + " mm"

cv2.putText(viz_list[i],string, (x, min(y+h +50, viz_list[i].shape[0]-25)), cv2.FONT_HERSHEY_SIMPLEX, 0.5, (0,0,255), 1)

# print(string)

else:

for i in range(len(viz_list)):

if viz_list_str[i][-1] == "1":

# Displaying the detected digestate/liquid height

cv2.line(viz_list[i], (x+(w//2), foam_edge), (x+(w//2),foam_edge+(liquid_height)), (0, 0, 255), 2)

string = "digestate height: " + str(round(true_liquid_height*1000,2)) + " mm"

cv2.putText(viz_list[i],string, (x, min(y+h +50, viz_list[i].shape[0]-25)), cv2.FONT_HERSHEY_SIMPLEX, 0.5, (0,0,255), 1)

# print(string)

for i in range(len(viz_list)):

if viz_list_str[i][-3] == "1":

# Displaying the detected foam height

cv2.line(viz_list[i], (x+(w//2), round(foam_bbox[1])), (x+(w//2), round(foam_bbox[3])), (0, 255, 0), 2)

string = "foam height: " + str(round(true_foam_height*1000,2)) + " mm"

cv2.putText(viz_list[i],string, (x, max(round(min(foam_bbox[1], foam_bbox[3]) -50), 25)), cv2.FONT_HERSHEY_SIMPLEX, 0.5, (0,255,0), 1)

# print(string)

# cv2.imshow("final_output", viz)

# cv2.waitKey(0)

# cv2.destroyAllWindows()

return viz_list, viz_list_str, colour, colour_foam, digestate_info

if __name__ == "__main__":

process_img()

## toBinary.py

Author(s): Ling Chen

import cv2

def toBinary(image):

"""

Function to convert an image to binary version using OTSU thresholding

:param image: The OpenCV cv::Mat BGR image

:returns: Binary image

"""

# Convert image to grayscale

gray = cv2.cvtColor(image, cv2.COLOR_BGR2GRAY)

# Apply Bilateral Blurring (to reduce noise while keeping edges sharp)

blur = cv2.bilateralFilter(gray, 5, 75, 75)

# Converting blurred image into binary image

thresh = cv2.threshold(blur, 0, 255, cv2.THRESH_BINARY_INV)[1]

# cv2.imshow('thresh',thresh)

return thresh

## rescale_frame.py

Author(s): Ling Chen

import cv2

# Rescaling image

def rescaleFrame(frame, scale):

"""

Function to rescale an image based on a scale ratio

:param frame: image to rescale

:param scale: positive float representing scale

:returns: rescaled image

"""

width = int(frame.shape[1] * scale)

height = int(frame.shape[0] * scale)

dimensions = (width, height)

return cv2.resize(frame, dimensions, interpolation=cv2.INTER_CUBIC)

## getEdges.py

Author(s): Ling Chen

import cv2

import numpy as np

def getEdges(image, blur):

"""

function to get the canny edges of an image after applying shapening and blurring.

:param image: image to find the edges

:param blur: odd number for the blur kernel

:returns: the edges from the image

"""

if blur%2 == 0:

raise Exception("Blur must be odd integer")

kernel = np.array([[0, -1, 0],

[-1, 5,-1],

[0, -1, 0]], )

image_sharp = cv2.filter2D(src=image, ddepth=-1, kernel=kernel)

# cv2.imshow('sharpened image', image_sharp)

# Apply Bilateral Blurring (to reduce noise while keeping edges sharp)

# blurred = cv2.bilateralFilter(image_sharp, blur, 75, 75)

blurred = cv2.GaussianBlur(image_sharp,(blur,blur),0)

canny_edges = cv2.Canny(blurred, 45, 155)

return canny_edges

## getBoundingBox.py

Author(s): Ling Chen

import cv2

from utils.getEdges import getEdges

from utils.toBinary import toBinary

def getBoundingBox(image):

binary = toBinary(image)

canny = getEdges(binary, 1)

# cv2.imshow("can", canny)

# cv2.imshow("bi",binary)

# cv2.imshow("ca",canny)

# cv2.waitKey(0)

contours, hierarchy = cv2.findContours(canny, cv2.RETR_TREE, cv2.CHAIN_APPROX_NONE)

contours = sorted(contours, key=cv2.contourArea, reverse=True)

best_contour = contours[0]

box = cv2.boundingRect(best_contour)

return box

## getFoamFromModel.py

Author(s): Ling Chen

import sys

sys.path.append("./foam_detection/detectron2-main/")

sys.path.append("./detectron2-main/")

import os

import pickle

from detectron2.engine import DefaultPredictor

from detectron2.utils.visualizer import Visualizer

from detectron2.utils.visualizer import ColorMode

import cv2

def getFoamFromModel(image):

cfg_save_path = "foam_mask_rcnn/IS_cfg.pickle"

with open(cfg_save_path, 'rb') as f:

cfg = pickle.load(f)

cfg.MODEL.WEIGHTS = os.path.join("foam_mask_rcnn/" + cfg.OUTPUT_DIR, "model_final.pth")

cfg.MODEL.ROI_HEADS.SCORE_THRESH_TEST = 0.2

predictor = DefaultPredictor(cfg)

outputs = predictor(image)

output_instance = outputs["instances"].to("cpu")

v = Visualizer(image[:,:,::-1], metadata={}, scale =1, instance_mode=ColorMode.SEGMENTATION)

v = v.draw_instance_predictions(output_instance)

detected_classes = output_instance.pred_classes.numpy().tolist()

# print(detected_classes)

bbox = None

if detected_classes != []:

try:

foam_idx = detected_classes.index(1)

except ValueError: # if there is no foam

return None, cv2.cvtColor(v.get_image(), cv2.COLOR_RGB2BGR)

else:

detected_bboxs = output_instance.pred_boxes.tensor.numpy().tolist()

bbox = detected_bboxs[foam_idx]

# mask = output_instance.pred_masks.numpy()

# print( mask.shape)

return bbox, cv2.cvtColor(v.get_image(), cv2.COLOR_RGB2BGR)

## getDigestateInfo.py

Author(s): Ling Chen

from utils.getEdges import getEdges

import cv2

def getDigestateInfo(image, box, foam_bbox, no_foam):

"""

Function to get various info on the digestate sample.

:param image: image of sample

:param box: bounding box coordinates of the flask

:param foam_bbox: bounding box of foam given in coordinates of top left and bottom right corners

:param no_foam: Boolean of whether there is foam or not

:returns: a dictionary containing various information of the sample

"""

canny = getEdges(image, 5)

# cv2.imshow("edges for digestate info", canny)

x,y,w,h = box

# print(box)

# plastic flask

# TRUE_FLASK_HEIGHT = 0.1421 #metres

# glass jar

TRUE_FLASK_HEIGHT = 0.135 #metres

# print( box)

# cv2.imshow("c", canny)

# cv2.waitKey(0)

if no_foam:

foam_height = None

foam_colour = None

ratio_foam_to_flask = 0

# get liquid height

for i in range(h):

if canny[y+h-(i+1)][x+(w//2)] == 255 and i>50:

liquid_height = i

break

liquid_colour = image[y+h-(liquid_height//2)][x+(w//2)]

else:

foam_height = round(abs(foam_bbox[3] - foam_bbox[1]))

foam_colour = image[round(abs(foam_bbox[3]-foam_bbox[1])//2)+round(min(foam_bbox[1], foam_bbox[3]))][x+(w//2)]

ratio_foam_to_flask = foam_height/h

# get liquid height

foam_edge = round(max(foam_bbox[3], foam_bbox[1]))

# print(foam_edge)

# print(y)

# print(h)

# print(foam_edge)

liquid_height = y+h-foam_edge

liquid_colour = image[foam_edge+(liquid_height//2)][x+(w//2)]

ratio_liquid_to_flask = liquid_height/h

digestate_info = {

"digestate height": liquid_height,

"digestate colour": liquid_colour,

"foam height": foam_height,

"foam colour": foam_colour,

"real foam height": ratio_foam_to_flask*TRUE_FLASK_HEIGHT,

"real digestate height": ratio_liquid_to_flask*TRUE_FLASK_HEIGHT

}

return digestate_info

## colourBlockDetection.py

Author(s): Ling Chen

# Python code for Multiple Color Detection

import numpy as np

import cv2

def colourBlockDetection(imageFrame, viz, bgr):

# Convert the imageFrame in

# BGR(RGB color space) to

# HSV(hue-saturation-value)

# color space

hsvFrame = cv2.cvtColor(imageFrame, cv2.COLOR_BGR2HSV)

bgr = np.uint8([[bgr]])

hsv = cv2.cvtColor(bgr, cv2.COLOR_BGR2HSV)

hsv = np.squeeze(np.squeeze(hsv))

# Set range for red color and

# define mask

h_thresh = 50

s_thresh = 70

v_thresh = 70

minHSV = np.array([hsv[0] - h_thresh, hsv[1] - s_thresh, hsv[2] - v_thresh])

if minHSV[0] <= 0:

minHSV[0] = 1

if minHSV[1] <= 0:

minHSV[1] = 1

if minHSV[2] <= 0:

minHSV[2] = 1

maxHSV = np.array([hsv[0] + h_thresh, hsv[1] + s_thresh, hsv[2] + v_thresh])

mask = cv2.inRange(hsvFrame, minHSV, maxHSV)

# Morphological Transform, Dilation

# for each color and bitwise_and operator

# between imageFrame and mask determines

# to detect only that particular color

kernal = np.ones((5, 5), "uint8")

# For red color

mask = cv2.erode(mask, kernal)

mask = cv2.dilate(mask, kernal, iterations=2)

res = cv2.bitwise_and(imageFrame, imageFrame, mask = mask)

# cv2.imshow("colour_mask", mask)

# print(hsv)

# print(minHSV)

# print(maxHSV)

# Creating contour of colour blob

contours, hierarchy = cv2.findContours(mask, cv2.RETR_TREE, cv2.CHAIN_APPROX_SIMPLE)

max_contour = sorted(contours, key = cv2.contourArea, reverse=True)[0]

if cv2.contourArea(max_contour) > 300:

x, y, w, h = cv2.boundingRect(max_contour)

viz = cv2.rectangle(viz, (x, y), (x + w, y + h), (255, 0, 0), 2)

# cv2.putText(viz, "Red Colour", (x, y), cv2.FONT_HERSHEY_SIMPLEX, 1.0, (0, 0, 255))

return viz

## client_pi.py

Author(s): Ling Chen

import os, socket, time, struct

HOST = "192.168.246.239" # Ling home wifi

HOST = "192.168.234.172" # Ling Hotspot

HOST = "172.20.10.8" # Kabir Hotspot

PORT = 52212

sock = socket.socket(socket.AF_INET, socket.SOCK_STREAM)

# sock.setsockopt(socket.SOL_SOCKET, socket.SO_REUSEADDR, 1)

#trying to connect to socket

# try:

sock.connect((HOST,PORT))

# Raspberry Pi sends over img it captures from pi-cam:

file_name = "foam_img.jpg"

file_len = os.stat(file_name).st_size

msg_header = struct.pack('<I', file_len)

sock.sendall(msg_header)

fd = open(file_name, 'rb')

data = fd.read(file_len)

while data:

sock.sendall(data)

data = fd.read(file_len)

fd.close()

# print("Image Sent To Host")

viz_list_str = ["viz0000", "viz0001", "viz0010", "viz0011", "viz0100", "viz0101", "viz0110", "viz0111", "viz1000", "viz1001", "viz1010", "viz1011", "viz1100", "viz1101", "viz1110", "viz1111"]

# Client recieves processed img from server

for i in range(16):

file_name = 'transferred_files/' + viz_list_str[i] + '.jpg'

msg_header = sock.recv(4)

while len(msg_header) != 4:

msg_header += sock.recv(4- len(msg_header))

file_len = struct.unpack('<I', msg_header)[0]

nFile = open(file_name, 'wb')

data = sock.recv(file_len)

while len(data) != file_len:

data += sock.recv(file_len - len(data))

nFile.write(data)

nFile.close()

# print("Image Recieved From Host")

file_name = "transferred_files/digestate_colour.jpg"

msg_header = sock.recv(4)

while len(msg_header) != 4:

msg_header += sock.recv(4- len(msg_header))

file_len = struct.unpack('<I', msg_header)[0]

nFile = open(file_name, 'wb')

data = sock.recv(file_len)

while len(data) != file_len:

data += sock.recv(file_len - len(data))

nFile.write(data)

nFile.close()

file_name = "transferred_files/foam_colour.jpg"

msg_header = sock.recv(4)

while len(msg_header) != 4:

msg_header += sock.recv(4- len(msg_header))

file_len = struct.unpack('<I', msg_header)[0]

nFile = open(file_name, 'wb')

data = sock.recv(file_len)

while len(data) != file_len:

data += sock.recv(file_len - len(data))

nFile.write(data)

nFile.close()

sock.close()

## server_host.py

Author(s): Ling Chen

import os, socket, time

from foam_detection.process_img import process_img

import cv2

import struct

# Creating socket

sock = socket.socket(socket.AF_INET, socket.SOCK_STREAM)

HOST = "0.0.0.0"

PORT = 52212

machine = socket.gethostbyname(socket.gethostname())

sock.bind((HOST, PORT))

sock.listen(3)

print("HOST: ", sock.getsockname())

print("Server is Listening...")

# Accepting the connection from the client

client, addr = sock.accept()

# Server recieves img from raspberry pi

# Client recieves processed img from server

file_name = 'transferred_files/foam_img_from_pi.jpg'

msg_header = client.recv(4)

while len(msg_header) != 4:

msg_header += client.recv(4- len(msg_header))

file_len = struct.unpack('<I', msg_header)[0]

nFile = open(file_name, 'wb')

data = client.recv(file_len)

while len(data) != file_len:

data += client.recv(file_len - len(data))

nFile.write(data)

nFile.close()

print("Image Recieved From Pi")

# Server processes img

img = cv2.imread("transferred_files/foam_img_from_pi.jpg")

viz_list, viz_list_str, digestate_colour, foam_colour, digestate_info = process_img(img)

for i in range(len(viz_list)):

cv2.imwrite("transferred_files/" +viz_list_str[i] + ".jpg", viz_list[i])

cv2.imwrite("transferred_files/digestate_colour.jpg", digestate_colour)

cv2.imwrite("transferred_files/foam_colour.jpg", foam_colour)

# Server sends processed img back to pi

for i in range(len(viz_list)):

file_name = "transferred_files/" + viz_list_str[i] + ".jpg"

file_len = os.stat(file_name).st_size

msg_header = struct.pack('<I', file_len)

client.sendall(msg_header)

fd = open(file_name, 'rb')

data = fd.read(file_len)

while data:

client.sendall(data)

data = fd.read(file_len)

fd.close()

print("Analyzed Image Sent To Client")

file_name = "transferred_files/digestate_colour.jpg"

file_len = os.stat(file_name).st_size

msg_header = struct.pack('<I', file_len)

client.sendall(msg_header)

fd = open(file_name, 'rb')

data = fd.read(file_len)

while data:

client.sendall(data)

data = fd.read(file_len)

fd.close()

print("Analyzed Image Sent To Client")

file_name = "transferred_files/foam_colour.jpg"

file_len = os.stat(file_name).st_size

msg_header = struct.pack('<I', file_len)

client.sendall(msg_header)

fd = open(file_name, 'rb')

data = fd.read(file_len)

while data:

client.sendall(data)

data = fd.read(file_len)

fd.close()

print("Analyzed Image Sent To Client")

client.close()

## maskRCNN_training.py

Author(s): Ling Chen

import torch

import torchvision

import cv2

import os

import numpy as np

import json

import random

import matplotlib.pyplot as plt

%matplotlib inline

# pip install 'git+https://github.com/facebookresearch/detectron2.git'

from detectron2.structures import BoxMode

from detectron2.data import DatasetCatalog, MetadataCatalog

from detectron2.utils.logger import setup_logger

from detectron2.data.datasets import register_coco_instances

from detectron2 import model_zoo

from detectron2.engine import DefaultTrainer, DefaultPredictor

from detectron2.config import get_cfg

from detectron2.utils.visualizer import ColorMode, Visualizer

from detectron2.utils.visualizer import Visualizer

from detectron2.utils.visualizer import ColorMode

import cv2

import pickle

#### Utils ####

def plot_samples(dataset_name, n=1):

dataset_custom = DatasetCatalog.get(dataset_name)

dataset_custom_metadata = MetadataCatalog.get(dataset_name)

for s in random.sample(dataset_custom, n):

img = cv2.imread(s["file_name"])

v = Visualizer(img[:,:,::-1], metadata=dataset_custom_metadata, scale = 1)

v = v.draw_dataset_dict(s)

plt.figure(figsize=(5,5))

plt.imshow(v.get_image())

plt.show()

def get_train_cfg(config_file_path, checkpoint_url, train_dataset_name, test_dataset_name, num_classes, device, output_dir):

cfg = get_cfg()

cfg.merge_from_file(model_zoo.get_config_file(config_file_path))

cfg.MODEL.WEIGHTS = model_zoo.get_checkpoint_url(checkpoint_url)

cfg.DATASETS.TRAIN = (train_dataset_name,)

cfg.DATASETS.TEST = (test_dataset_name,)

cfg.DATALOADER.NUM_WORKERS = 2

cfg.SOLVER.IMS_PER_BATCH = 5

cfg.SOLVER.BASE_LR = 0.00025

cfg.SOLVER.MAX_ITER = 3000

cfg.SOLVER.STEPS = []

cfg.MODEL.ROI_HEADS.NUM_CLASSES = num_classes

cfg.MODEL.DEVICE = device

cfg.OUTPUT_DIR = output_dir

return cfg

def on_image(image_path, predictor):

im = cv2.imread(image_path)

outputs = predictor(im)

print(outputs)

v = Visualizer(im[:,:,::-1], metadata={}, scale =1, instance_mode=ColorMode.SEGMENTATION)

v = v.draw_instance_predictions(outputs["instances"].to("cpu"))

plt.figure(figsize=(5,5))

plt.imshow(v.get_image())

plt.show()

## If doing instance segmentation:

config_file_path = "COCO-InstanceSegmentation/mask_rcnn_R_50_FPN_3x.yaml"

checkpoint_url = "COCO-InstanceSegmentation/mask_rcnn_R_50_FPN_3x.yaml"

output_dir = "./output"

num_classes = 2

device = "cpu"

train_dataset_name = "LP_train"

train_images_path = "train"

train_json_annot_path = "train/_annotations.coco.json"

test_dataset_name = "LP_valid"

test_images_path = "valid"

test_json_annot_path = "valid/_annotations.coco.json"

cfg_save_path = "IS_cfg_cpu.pickle"

register_coco_instances(name = train_dataset_name, metadata={}, json_file=train_json_annot_path, image_root=train_images_path)

register_coco_instances(name = test_dataset_name, metadata={}, json_file=test_json_annot_path, image_root=test_images_path)

# plot_samples(train_dataset_name)

cfg = get_train_cfg(config_file_path, checkpoint_url, train_dataset_name, test_dataset_name, num_classes, device, output_dir)\

with open(cfg_save_path, 'wb') as f:

pickle.dump(cfg, f, protocol=pickle.HIGHEST_PROTOCOL)

os.makedirs(cfg.OUTPUT_DIR, exist_ok=True)

trainer = DefaultTrainer(cfg)

trainer.resume_or_load(resume = False)

trainer.train()

cfg_save_path = "IS_cfg_cpu.pickle"

with open(cfg_save_path, 'rb') as f:

cfg = pickle.load(f)

cfg.MODEL.WEIGHTS = os.path.join(cfg.OUTPUT_DIR, "model_final.pth")

cfg.MODEL.ROI_HEADS.SCORE_THRESH_TEST = 0.3

print(cfg.MODEL.DEVICE)

predictor = DefaultPredictor(cfg)

def test_output(dataset_name, n=1):

dataset_custom = DatasetCatalog.get(dataset_name)

dataset_custom_metadata = MetadataCatalog.get(dataset_name)

for s in random.sample(dataset_custom, n):

on_image(s["file_name"], predictor)

# test_output(test_dataset_name, 5)

image_path = "fg3.jpg"

on_image(image_path, predictor)

# Remote Control Web-app

## index.php

Author(s): Kabir Chugh, Ling Chen

<?php

if (isset($_POST['next'])){

header("Location: main.php");

exit();

}

?>

<html>

<head><link rel = "stylesheet" href = "main.css"></head>

<div class = "top ">

<font><center><b> <p class = "header_text">Welcome to Team 232 Demonstration</p><b></center></font>

</div>

<div class = "below_top">

</div>

<br><br><br>

<center>

<img src = "device.jpg" width="800" height="1000" alt="Team Logo">

<br><br><br>

</div>

<div class = "below_top">

</div>

<div class = "below_top">

<form method="post">

<button name = "next">

<p class ="button_text">Start Sampling</p>

</button>

</form>

<br>

</font>

<script>

</script>

</html>

## main.php

Author(s): Kabir Chugh, Ling Chen

<?php

$weight = "---";

$warning_message = "";

if (isset($_POST['b7']))

{

$warning_message = "Calculating Weight...";

// Get tilt using script

shell_exec('python3 MPU.py');

$file = fopen("angle_x.txt","r");

$tilt_x = fread($file, filesize("angle_x.txt"));

fclose($file);

$file = fopen("angle_y.txt","r");

$tilt_y = fread($file, filesize("angle_y.txt"));

fclose($file);

$tilt_x = intval($tilt_x);

$tilt_y = intval($tilt_y);

$tilt_inbound_x = ($tilt_x <15 and $tilt_x >-15);

$tilt_inbound_y = ($tilt_y <15 and $tilt_y >-15);

$tilt_inbound = $tilt_inbound_x and $tilt_inbound_y;

if(! $tilt_inbound)

{

$weight = "---";

$warning_message = "Plaform is tilted!";

} else

{

// Get weight using scripts

shell_exec('python3 MAIN2.py');

$file = fopen("weights.txt","r");

$weight = fread($file, filesize("weights.txt"));

fclose($file);

$valid_weight = True;

foreach (str_split($weight) as $char) {

if (($char != ".")and ($char != "0") and ($char != "1") and ($char != "2") and ($char != "3") and ($char != "4") and ($char != "5") and ($char != "6") and ($char != "7") and ($char != "8") and ($char != "9")){

$valid_weight = False;

break;

}

}

$weight_inbound = $weight>140 and $weight<160;

if ($valid_weight){

if ($weight_inbound)

{

$warning_message = "Weight is within bounds";

} else

{

$warning_message = "The weight of the given sample is out of bounds of 140g and 160g.";

}

}

else {

$warning_message = $weight;

$weight = "---";

}

}

}

if (isset($_POST['next'])){

// Get tilt using script

shell_exec('python3 MPU.py');

$file = fopen("angle_x.txt","r");

$tilt_x = fread($file, filesize("angle_x.txt"));

fclose($file);

$file = fopen("angle_y.txt","r");

$tilt_y = fread($file, filesize("angle_y.txt"));

fclose($file);

$tilt_x = intval($tilt_x);

$tilt_y = intval($tilt_y);

$tilt_inbound_x = ($tilt_x <15 and $tilt_x >-15);

$tilt_inbound_y = ($tilt_y <15 and $tilt_y >-15);

$tilt_inbound = $tilt_inbound_x and $tilt_inbound_y;

if ($tilt_inbound){

// Get weight using scripts

shell_exec('python3 MAIN2.py');

$file = fopen("weights.txt","r");

$weight = fread($file, filesize("weights.txt"));

fclose($file);

$valid_weight = True;

foreach (str_split($weight) as $char) {

if (($char != ".")and ($char != "0") and ($char != "1") and ($char != "2") and ($char != "3") and ($char != "4") and ($char != "5") and ($char != "6") and ($char != "7") and ($char != "8") and ($char != "9")){

$valid_weight = False;

break;

}

}

$weight_inbound = $weight>140 and $weight<160;

if ($weight_inbound){

header("Location: servo.php");

exit();

} else {

$warning_message = "Make sure weight is within 140-160 grams before proceeding!";

}

} else {

$warning_message = "Make sure platfrom is flat before proceeding!";

}

}

?>

<html>

<head>

<link rel = "stylesheet" href = "main.css">

</head>

<body>

<div class = "top ">

<font><center><b> <p class = "header_text">Measure Weight</p><b></center></font>

</div>

<div class = "below_top">

</div>

<div class = "below_top">

</div>

<div class = "below_top">

</div>

<div class = "below_top">

</div>

<center>

<form method = "post">

<button name = "b7" id="function_btn">

<p class ="button_text">Display weight </p>

</button>

<br><br>

<p>

The weight of the given sample is:

</p>

<div class = "separator"></div>

<p class = "sec">

<?=$weight ?> grams

</p>

<div class = "separator"></div>

<p class = "warning">

<?=$warning_message ?>

</p>

<br><br><br>

<br>

<button name="next">

<p class ="button_text">Next</p>

</button>

</form>

</center>

<script type = "text/javascript" >

</script>

</body>

</html>

## servo.php

Author(s): Kabir Chugh, Ling Chen

<?php

$img = "";

$warning_message = "";

if (isset($_POST['b1'])){

// Get tilt using script

shell_exec('python3 MPU.py');

$file = fopen("angle_x.txt","r");

$tilt_x = fread($file, filesize("angle_x.txt"));

fclose($file);

$file = fopen("angle_y.txt","r");

$tilt_y = fread($file, filesize("angle_y.txt"));

fclose($file);

$tilt_inbound = ($tilt_x <15 and $tilt_x >-15) and ($tilt_y <15 and $tilt_y >-15);

if ($tilt_inbound){

$warning_message = "";

shell_exec('python3 Servo_0.py');

} else {

$warning_message = "Platform is too tilted!";

}

}

if (isset($_POST['b2'])){

// Get tilt using script

shell_exec('python3 MPU.py');

$file = fopen("angle_x.txt","r");

$tilt_x = fread($file, filesize("angle_x.txt"));

fclose($file);

$file = fopen("angle_y.txt","r");

$tilt_y = fread($file, filesize("angle_y.txt"));

fclose($file);

$tilt_inbound = ($tilt_x <15 and $tilt_x >-15) and ($tilt_y <15 and $tilt_y >-15);

if ($tilt_inbound){

$warning_message = "";

shell_exec('python3 Servo_45.py');

} else {

$warning_message = "Platform is too tilted!";

}

}

if (isset($_POST['b3'])){

// Get tilt using script

shell_exec('python3 MPU.py');

$file = fopen("angle_x.txt","r");

$tilt_x = fread($file, filesize("angle_x.txt"));

fclose($file);

$file = fopen("angle_y.txt","r");

$tilt_y = fread($file, filesize("angle_y.txt"));

fclose($file);

$tilt_inbound = ($tilt_x <15 and $tilt_x >-15) and ($tilt_y <15 and $tilt_y >-15);

if ($tilt_inbound){

$warning_message = "";

shell_exec('python3 Servo_90.py');

} else {

$warning_message = "Platform is too tilted!";

}

}

if (isset($_POST['b4'])){

// Get tilt using script

shell_exec('python3 MPU.py');

$file = fopen("angle_x.txt","r");

$tilt_x = fread($file, filesize("angle_x.txt"));

fclose($file);

$file = fopen("angle_y.txt","r");

$tilt_y = fread($file, filesize("angle_y.txt"));

fclose($file);

$tilt_inbound = ($tilt_x <15 and $tilt_x >-15) and ($tilt_y <15 and $tilt_y >-15);

if ($tilt_inbound){

shell_exec('python3 Servo_135.py');

} else {

$warning_message = "Platform is too tilted!";

}

}

if (isset($_POST['b5'])){

// Get tilt using script

shell_exec('python3 MPU.py');

$file = fopen("angle_x.txt","r");

$tilt_x = fread($file, filesize("angle_x.txt"));

fclose($file);

$file = fopen("angle_y.txt","r");

$tilt_y = fread($file, filesize("angle_y.txt"));

fclose($file);

$tilt_inbound = ($tilt_x <15 and $tilt_x >-15) and ($tilt_y <15 and $tilt_y >-15);

if ($tilt_inbound){

$warning_message = "";

shell_exec('python3 Servo_180.py');

} else {

$warning_message = "Platform is too tilted!";

}

}

if(True){

// shell_exec('python3 camera_image.py');

// $file = fopen("img_num.txt","r");

// $img_num= fread($file, filesize("img_num.txt"));

//fclose($file);

//$file_name = "images/foam_img".$img_num.".png";

sleep(1);

$img = '<center> <img src = foam_img.jpg alt = "Sample Image"></center>';

}

if (isset($_POST['pic'])){

// Get tilt using script

shell_exec('python3 MPU.py');

$file = fopen("angle_x.txt","r");

$tilt_x = fread($file, filesize("angle_x.txt"));

fclose($file);

$file = fopen("angle_y.txt","r");

$tilt_y = fread($file, filesize("angle_y.txt"));

fclose($file);

$tilt_inbound = ($tilt_x <15 and $tilt_x >-15) and ($tilt_y <15 and $tilt_y >-15);

if ($tilt_inbound){

$warning_message = "Analyzing...";

shell_exec('python3 client_pi.py');

header("Location: foam.php");

exit();

} else {

$warning_message = "Platform is too tilted!";

}

}

?>

<html>

<head>

<link rel = "stylesheet" href = "main.css">

</head>

<body>

<div class = "top ">

<font><center><b> <p class = "header_text">Capture Image</p><b></center></font>

</div>

<div class = "below_top">

</div>

<center>

<?= $img ?>

<br><br>

<div class = "separator"></div>

<form method = "post">

<p>Select the angle for servo rotation:</p>

<div class = "button_row">

<button name = "b1" id="function_btn1">

<p class ="button_text"> 0 &nbsp &nbsp Degrees </p>

</button>

&nbsp &nbsp

<button name = "b2" id="function_btn2">

<p class ="button_text"> 45 &nbsp Degrees </p>

</button>

</div>

<div class = "button_row">

<button name = "b3" id="function_btn1" >

<p class ="button_text">90 &nbsp Degrees</p>

</button>

&nbsp &nbsp

<button name = "b4" id="function_btn2">

<p class ="button_text">135 &nbsp Degree</p>

</button>

</div>

<div class = "button_row">

<button name = "b5" id="function_btn3">

<p class ="button_text">180 Degrees</p>

</button>

</div>

<br><br>

<div class = "separator"></div>

<br><br>

<button name = "pic" onClick = redirectToMain()>

<p class ="button_text">Analyse Image</p>

</button>

<br><br>

<?=$warning_message ?>

</form>

</center>

<script type = "text/javascript" >

function redirectToMain()

{

window.location.replace("foam.php")

}

</script>

</body>

</html>

## foam.php

Author(s): Kabir Chugh, Ling Chen

<?php

$digestate = '<img src = transferred_files/digestate_colour.jpg alt = "digestate colour" style="width:300px; height:100px; margin-left:125px">';

$foam = '<img src = transferred_files/foam_colour.jpg alt = "foam colour" style="width:300px; height:100px; margin-left:125px">';

if (isset($_POST['pic'])){

header("Location: servo.php");

exit();

}

if (isset($_POST['foam'])){

if (isset($_POST['foam_height'])){

if (isset($_POST['digestate'])){

if (isset($_POST['digestate_height'])){

//1111

$img = '<img src = transferred_files/viz1111.jpg alt = "Sample Image">';

} else {

//1110

$img = '<img src = transferred_files/viz1110.jpg alt = "Sample Image">';

}

} else {

if (isset($_POST['digestate_height'])){

//1101

$img = '<img src = transferred_files/viz1101.jpg alt = "Sample Image">';

} else {

//1100

$img = '<img src = transferred_files/viz1100.jpg alt = "Sample Image">';

}

}

} else {

if (isset($_POST['digestate'])){

if (isset($_POST['digestate_height'])){

//1011

$img = '<img src = transferred_files/viz1011.jpg alt = "Sample Image">';

} else {

//1010

$img = '<img src = transferred_files/viz1010.jpg alt = "Sample Image">';

}

} else {

if (isset($_POST['digestate_height'])){

//1001

$img = '<img src = transferred_files/viz1001.jpg alt = "Sample Image">';

} else {

//1000

$img = '<img src = transferred_files/viz1000.jpg alt = "Sample Image">';

}

}

}

} else {

if (isset($_POST['foam_height'])){

if (isset($_POST['digestate'])){

if (isset($_POST['digestate_height'])){

//0111

$img = '<img src = transferred_files/viz0111.jpg alt = "Sample Image">';

} else {

//0110

$img = '<img src = transferred_files/viz0110.jpg alt = "Sample Image">';

}

} else {

if (isset($_POST['digestate_height'])){

//0101

$img = '<img src = transferred_files/viz0101.jpg alt = "Sample Image">';

} else {

//0100

$img = '<img src = transferred_files/viz0100.jpg alt = "Sample Image">';

}

}

} else {

if (isset($_POST['digestate'])){

if (isset($_POST['digestate_height'])){

//0011

$img = '<img src = transferred_files/viz0011.jpg alt = "Sample Image">';

} else {

//0010

$img = '<img src = transferred_files/viz0010.jpg alt = "Sample Image">';

}

} else {

if (isset($_POST['digestate_height'])){

//0001

$img = '<img src = transferred_files/viz0001.jpg alt = "Sample Image">';

} else {

//0000

$img = '<img src = transferred_files/viz0000.jpg alt = "Sample Image">';

}

}

}

}

?>

<html>

<head>

<link rel = "stylesheet" href = "main.css">

</head>

<body>

<div class = "top ">

<font><center><b> <p class = "header_text">Analysis Results</p><b></center></font>

</div>

<div class = "below_top">

</div>

<center><?=$img?></center>

<div class = "below_top">

</div>

<div style="width:100%; overflow: hidden;">

<div style = "width:500px; float: left;">

<p class = "colour"> Foam Colour: </p>

<?=$foam?>

<br>

<p class = "colour"> Digestate Colour: </p>

<?=$digestate?>

</div>

<div style = "margin-left: 550px; margin-top: 0;">

<p> Display Options: </p>

<form method = "post">

<input type ="checkbox" name = "foam" >

<label for ="foam" class = "cform">Foam Area</label><br><br>

<input type ="checkbox" name = "foam_height">

<label for ="foam_height" class = "cform">Foam Height</label><br><br>

<input type ="checkbox" name = "digestate">

<label for ="digestate" class = "cform">Digestate Area</label><br><br>

<input type ="checkbox" name = "digestate_height">

<label for ="digestate_height" class = "cform">Digestate Height</label><br><br>

<br>

<button name = "submit" onClick = submit()>

<p class ="button_text">Submit</p>

</button> <br>

</div>

</div>

<center>

<br><br>

<div class = "separator"></div>

<br><br>

<button name = "pic">

<p class ="button_text">Retake Image</p>

</button>

</form>

</center>

</body>

</html>

<script>

/*

document.addEventListener('DOMContentLoaded',()=>{

let chk=document.querySelector('input[type="checkbox"][name="foam"]');

chk.checked=localStorage.getItem( chk.name )==null || localStorage.getItem( chk.name )=='false' ? false : true;

chk.addEventListener('click',e=>{

localStorage.setItem( chk.name, chk.checked )

//location.reload();

});

});

function set_state(){

*/

}

</script>

## main.css

Author(s): Kabir Chugh, Ling Chen

button{

font-size: 30px;

transition-duration: 0.4s;

background-color: #242526;

border: 2px solid #242526;

border-radius: 6px;

padding: 5px 100px 0 100px ;

}

button:hover{

background-color: #3a3b3c;

}

p{

font-size: 40px;

color: #E4E6EB;

font-weight: normal;

font-family: 'Arial';

}

.button_text{

font-size: 30px;

color: #E4E6EB;

}

body{

background-color: #18191A;

}

.header_text{

font-size: 50px;

font-weight: normal;

font-family: 'Arial';

color: #E4E6EB;

padding: 0 20px 0 20px;

}

.header_text2{

font-size: medium;

font-weight: bold;

font-family: 'Courier New', Courier, monospace;

color: rgb(0,255,255);

}

.header_text3{

font-size: medium;

font-weight: bold;

font-family: 'Courier New', Courier, monospace;

color: rgb(0,255,255);

}

.header_text4{

font-size: medium;

font-weight: bold;

font-family: 'Courier New', Courier, monospace;

color: rgb(0,255,255);

}

.container{

display: flex;

justify-content: space-around;

}

.top{

padding: 50px 0;

background-color: #242526;

}

.below_top{

padding: 25px 0;

}

.sec{

font-size: 40px;

color: #BOB3B8;

}

.warning{

font-size: 35px;

color: #7f0000;

padding: 0 20px 0 20px;

}

.separator{

background-color: #242526;

padding: 0 100px 0 100px;

height: 10px

}

.button_row{

padding: 10px 0 10px 0;

}

.colour{

font-size: 35px;

margin-left: 125px;

}

.cform{

font-size: 35px;

font-weight: normal;

font-family: 'Arial';

color: #E4E6EB;

}

input.largerCheckbox {

width: 30px;

height:30px;

}

## Servo[0-180].py

Author(s): Jason Ltg

from gpiozero import Servo

import math

from time import sleep

from gpiozero.pins.pigpio import PiGPIOFactory

factory = PiGPIOFactory()

servo = Servo(17, min_pulse_width = 0.5/1000, max_pulse_width = 2.33/1000, pin_factory=factory)

try:

angle = 180 #CHANGE THIS VALUE TO WHATEVER ANGLE NEEDED

servo.value = math.cos(math.radians(angle)) * -1

sleep(1)

except KeyboardInterrupt:

#Add extra here for safety upon "Ctrl + C" keyboard input exit

print("Goodbye!")

Note: Other files needed for web-app are omitted as they are just slight variations of the code shown in sections 1 to 4.

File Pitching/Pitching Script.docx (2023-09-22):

Questions to answer: [Aim for 225 words per section] [Also work on your slides]

1) What is the problem? [Kabir]

Anaerobic digestion is a method that helps convert organic load into a mixture gas mainly composed of methane (CH4) and carbon dioxide (CO2) through the action of bacteria. Anaerobic Digesters have been traditionally used for waste treatment since the produced methane is a useful source of energy. Anaerobic digesters are considered a complex system which usually undergoes failure. It is mostly due to one of the several problems such as high maintenance costs and the constant requirement of monitoring the foaming of the digest. Some foam is always present in anaerobic digesters which is a result of methane production in an anaerobic process. Generally, acids produced during the process lower the surface tension of an anaerobic digester. This allows for greater quantities of gas to be trapped at the surface of the digest which would lead to loss of several important gases. The foam can be controlled if monitored and seen at the right time during the process. The process is mainly used for the production of biogas, which is mostly methane gas. Methane, in a purer form, is known as natural gas when piped into our homes and businesses, so biogas can be used as an energy source. Hence, this process is of great importance.So, our system will be useful in testing the digestate during all stages of Anaerobic digestion in a very efficient manner.

2) How are we solving the problem with our device? [Ritchie]

Our team has designed a device to monitor the foaming characteristics and colour of the digestate. The device takes in a sample of the Digestate from the tank and shows the user a picture of the digestate sample and the thickness of the foam.

a) How a user would operate the device

-Our AD sample tester is a portable cylindrical device, it has a handle which allows the user to move the device around

-at the top of the device, there’s a threaded tube which allows the device to be fastened to the tap

-First, the user should securely fasten the device onto the tap. Then turn on the power and follow the instructions on the interface to go through the testing process

- after the test is complete, the user can clean the device

- First, switch the power off, then remove the device from the tap

- open the cover at the bottom to let the liquid out

-Finally, flush the device from the top to bottom with cleaning agent, then rinse it with water in a similar way

3) Explain the functionalities of each part
  a) User interface (phone) [John]

There is a power on switch for the device, which acts as our reliable physical stop/ start function. There will also be an LED turning on to indicate the device is powered, hence the analysis preparations can begin.

Using a web app as the main point of control, the device is able to be remotely controlled using a mobile phone. By utilising a local area network wifi, live streaming of data is available over any devices that has access to a web browser. The layout of the web-app follows the flow of operation of the user, with options to return to their previous selection.

Pressing ‘Enter Sampling’ allows the user to prepare an appropriate sample and the environment needed for the testing. It then prompts the user to fill the flask to an appropriate mass, using the onboard scale and limit checking system. The user can change the rotation of the servo, and show the camera view. If the tilt, acceleration or velocity of the inertial measurement unit is too high, an error message will be displayed. If all conditions are met, the ‘Start Analysis’ button will perform image processing to output digestate colour and the associated foam length. Lastly, a download report button will allow the user to download a pdf file containing the results.

  b) Load cell, Servo [Jason]

In the proof of concept, the implementation of a servomotor was intended to allow the rotation of the vial containing the digestate and foam.

[Gif of servomotor moving and Gif of servomotor stuttering wait for Ling, so prepare the code]

By utilizing hardware based timed sampling, accurate rotational positioning was achieved, and jittering, which software based introduced, was eliminated

[Foam image at different perspectives? Think again, just grab some foam images of different characteristics…]

This enables the Pi-camera to capture images at multiple rotational positions to ensure consistent digestate and foam levels, and by extension, improves analysis.

However, from empirical testing, it was observed that in most situations, a significant difference in height was not detected. Hence the servomotor was not implemented. However, to combat cases of significant foam height variance, a secondary camera has been installed to compensate for this.

[Diagram of tap and CAD design, like Ritchie’s is okay]

In addition, with how the device works, by attaching itself to the reactor’s straight tap that dispenses the digestate, it minimizes variation in foam height and encourages flatness.

[Photo of the CAD Design wait for a 2nd camera to be in the CAD]

Therefore, in our final proposed mechanical design, a servomotor was not implemented. This provides a more robust design as lack of moving components results in increased longevity of the device and reduced maintenance.

[Photo of load cell in proof-of-concept and in the CAD?]

The load cell permits weight measurement of the digestate. Weight from the digestate is converted to a downwards force, which apply small amounts of tension and compression at the top and bottom of the load cell. This translates to minute changes in resistance, that when implemented into a Wheatstone bridge, will produce a measured voltage. This signal after calibration, consequently, outputs the measured weight of the digestate.

  c) Camera, pi computer [Ling]

The design comes equipped with a raspberry pi which serves as the brain of the device. It can directly communicate with our web app and allow the user to control various device functions remotely and intuitaively.

The raspberry pi Model 4B is chosen for this purpose as it is computationally powerful and would reliably execute any user inputs with little delay while also being extremely light weight at 50 grams.

To help analyze the digestate, we utilize the light-weight pi camera which will be directly connected to raspberry pi module and provide live high resolution images of the extracted digestate.

Firstly, by making effective use of efficient pre-existing AI methods, the background is removed to help reduce background interference during image analysis, greatly increasing the analysis accuracy.

Then by leveraging various computer vision techniques and utilizing our custom trained foam detection neural network, crucial characteristics of the digestate are detected, including, but not limited to region of foam, amount of foam, colour of foam, and the colour and amount of the digestate liquid.

These information are displayed in an intuitive way to the user through the mobile web app, where annotations of images taken directly from the pi camera can be viewed.

4) How the future device relates to the proof of concept? [Xavier]

Hi, my name is Xavier and I will show you through the main strengths of our design, and discuss modifications from our proof of concept.

Our design was created to be lightweight, portable, robust, and as safe as possible for our customers to use.

Let’s dive in.

*Many competitor products involve removing the digestate from the reactors, placing this into some temporary capsule, and then transporting this digestate to the testing instrument. *This is poor practice because it is slow, may result in a loss of temperature and digestate state change, and also exposes employees to potential spillages, which can carry hazardous gases and pathogens.

*Our design has flipped this, and instead we bring our instrument to the digestate and remove required human and digestate interaction. *From the get go, this has two major benefits, being:

- Time saved for workers from not having to move the digestate itself; and
- Reduction in the risks of spills occurring.

So, how is this achieved?*

We have done this through designing our unit so that it is screwed into bioreactor release valves that are required at customer sites. *Valve heads will be modular and we will customise to our client needs, meaning the instrument can work at any customer site, all over the world.

*For the general design, let’s highlight the main value adds to our customers:

- The unit is made of a Lightweight, but sturdy hard plastic outer shell
- there is a Comfortable rubber grip for easy transporting
- The instrument is well-sized, with a at 20cm round diameter, meaning it is small and compact
- The Total unit height is 24 cm, meaning it is easy to store on workplace shelves.
- It has an expected manufactured and assembled weight of 2.5kg, perfect for carrying purposes
- Battery operated, with an expected 24 hours of live testing before requiring recharging
- Designed for easy assembly and servicing

*As discussed previously, the design has two solenoid valves on either end of the central glass vial unit that control the fluid entering and exiting. *This allows fluid to be tapped directly from bioreactors, without any user intervention in between, and is tested immediately. *The glass uses the same concept as double-glazed windows, with a thick, outer layer, and a thin, inner layer of glass with a sealed gap of air between. At 100mL of digestate in the vial, the fluid is halfway up the container *The double glazed effect serves to insulate the digestate and maintain it in the mesophilic state during testing, and also serves to add extra strength to the glass container.

Now that digestate is in the container, how do we get it out?

*Compared to our competitors, the removal of tested digestate is simple, fast, and above all safe. This is accomplished through a simple, three stage process. *First, the user attaches a digestate waste bag, a product that we will design and sell to customers, to the bottom of the unit. *Next, the user will select the “remove waste” button after testing has finished, and the contents will be emptied out. *Finally, the user seals the bag, removes it from the container, and disposes of it into an appropriate hazardous waste bin.

*On top of added safety and time-saving benefits, the other major benefits of our product design are that:

- *Compared to standard tabletop designs, it does not need a flat surface to rest on;
- *Cannot be interrupted from knocks or movement, as it is screwed into place;
- *Does not require any heating and only requires insulation, as the digestate is immediately tested after it leaves the reactor, reducing costs;
- *That it opens the opportunity for an ongoing sales relationship with the customer through the need to purchase digestate waste bags;
- *And finally, there are minimal active and moving components, meaning that not only manufacturing, but also service costs will be reduced from the lack of components that are likely to break down.

Our design will save customers time, provide robust analysis, and be the safest product on the market.

End recording

Now, moving on to how this design differs from the proof of concept.

As mentioned previously, the servomotor used in the proof of concept did not make it into the final design. The advantage of having a rotating fluid container is that it reduces the risk of uneven foaming being undetected, as the camera would be able to survey angles at the same height.

Through empirical testing on the proof of concept, it was found that by surveying from two angles, both at 90 degrees from each other, this allowed sufficient information to accurately estimate the foam in the fluid container. Therefore, to reduce costs and expected mechanical failures in the field, the servomotor was replaced with a second camera at 90 degrees from the other. This ensures a robust, cheaper product that still gains the required information for diagnostic purposes.

Furthermore, as the risk of bumps or knocks actually moving the unit is very low, the IMU was not included in this design.

5) How do we stand out from the competition (cost and specs need to be mentioned)? [Xavier]

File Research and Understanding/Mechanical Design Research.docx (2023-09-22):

# Purpose

The purpose of this document is to provide supporting research for the mechanical design. Specifically, it looks to cover:

- Questions surrounding the digestate, like:
  - How biohazardous is it? What safety precautions are required for this?
    - Heavy influence on design
  - Appropriate disposal
  - Can it be cleaned out? How easy/difficult would it be to do so?
  - Does the digestate need to be kept in an environment with no/little oxygen?
  - Does the digestate have a certain pressure that it should be maintained at?
- Questions surrounding how to get the fluid into the container?
  - I’m personally a big fan of attaching the unit to the tap output.
  - Could also secure some sort of lead, but then this introduces more hazards.
  - Can assume, with some good reason, that we’d be able to place it onto a table
    - Flaws with this idea
- Questions surrounding how we will dispose of the fluid
  - Single use containers? Even then, how will the handler get these out safely?
    - Costs?
    - How would this affect how the heating elements are placed into the mixture?
  - Is there some sort of liquid solution that we could use to clean it out with?
    - What are the hazards of this? Costs?
- How we will configure the instrument for best analysis
  - This will be supported by some of the findings of ours
  - For example, does rotating get better foaming analysis accuracy?
    - Would we install rotation/stirring then, or just get multiple cameras?
    - How does the digestate actually foam?

# The digestate

https://www.epa.gov/agstar/how-does-anaerobic-digestion-work

## How biohazardous is it? What safety precautions are required for this?

Digestate can contain pathogens found in the inputs. These pathogens, if in contact with humans, can be extremely dangerous. As such, it should be ensured that no contact is made with the digestate.

Further, the digestate can contain:

- Ammonium (NH4)

And the biogas can include:

- Methane (CH4) - colourless, odourless, can cause asphyxiation
- C02 - colourless, odourless, can cause asphyxiation
- Hydrogen sulfide (H2S) - Rotten egg smell, colourless, but sensitivity to smell decreases rapidly with increasing concentrations. Attacks the central nervous system causing loss of consciousness and/or death.
- Ammonia (NH3) - Colourless gas with a strong pungent odour. Can cause lung damage and death in cases of high exposure to high concentrations..
- Carbon Monoxide (CO) - Binds with red blood cells, does not let oxygen bond to cells. Causes death through suffocation.

These gases are unlikely to come through in large quantities, but it’s best not to let them through.

Another interesting thing is that the digestate can be in the form of:

- A liquid
- A slurry
- Less commonly a stackable material that looks like compost

## Cleaning out the digestate

### Impacts on design

## Appropriate disposal

## Can it be cleaned out? How easy/difficult would it be to do so?

## Does the digestate need to be kept in an environment with no/little oxygen?

## Does the digestate have a certain pressure that it should be maintained at?

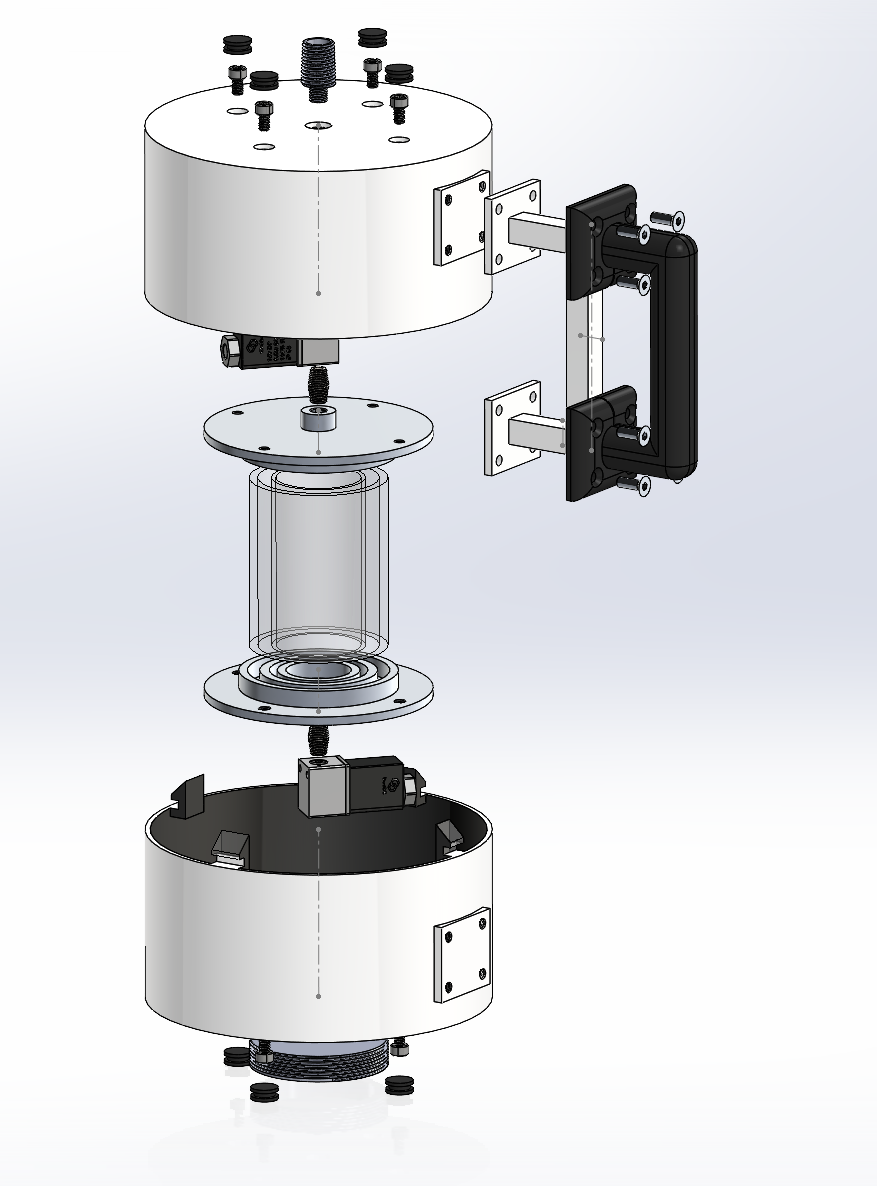
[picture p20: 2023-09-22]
Design/Report Images/Expanded View - Mechanical 2.png

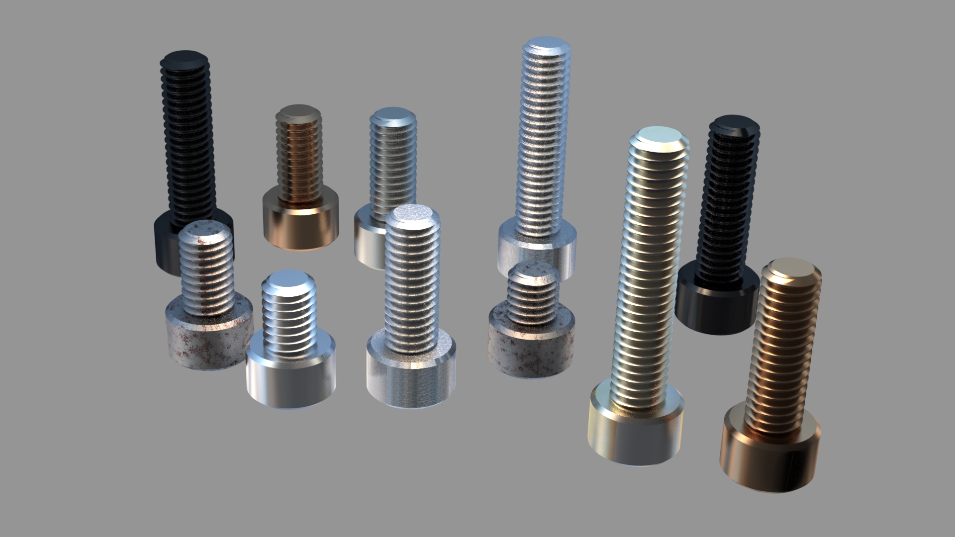
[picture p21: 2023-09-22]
Solidworks files/DESIGN/Bolts/Untitled Project.jpg

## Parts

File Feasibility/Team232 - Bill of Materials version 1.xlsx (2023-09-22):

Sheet: BOM
Bill of Materials (BOM)
Product Name : | AD tester device (T232's Instrument)
Assembly Name : | A1722 |  |  |  |  |  |  |  |  | [42]
Authors: | Ritchie Leong, Jason Ung, Xavier Andueza, Ling Chen, Kabir Chugh, John Nguyen
Assembly Revision : | 21
Approval Date : | 2022-10-07
Part ID | Part Name | Category | Description | Critical | Qty | Units | Phase | Process | Procurement | Vendor | MOQ | Lead Time (days) | Fixed Cost | Unit Cost | Cost
17221 | RASPBERRY PI 4 MODEL B 4GB SDRAM | PCB | Microcomputer | Y | 1 | each | In Design | PCB | MTS | Digikey | 1 | 7 | $88.09 | $88.09 | $88.09
17222 | 10mm 24V DC Solenoid Valve | Peripheral | 12V DC valve to control the input/output of liquids | Y | 2 | each | In Design |  | MTS | wicvaluve (Ebay) | 1 | 6 | $99.00 | $49.50 | $99.00
17223 | Bottom Attachment | Metal Threaded connector | Thread to connect waste container (Aluminium 6061-T6) | Y | 1 | each | In Design | CNC | OTS | Partzpro | 1 | 18 | $54.00 | $54.00 | $54.00
17224 | Camera screw | Fasteners | Screws to fasten camera to the cover (ABS Cinmei PA-757) | Y | 8 | each | RTS | Injection mold | MTS | ICOMold | 100 | 15 | $146.00 | $1.46 | $11.68
302201 | Camera, LED holder | Mount | Camera mount to hold the camera (304 Stainless Steel) | Y | 2 | each | In Design | CNC | OTS | Partzpro | 2 | 11 | $193.00 | $96.50 | $193.00
302301 | GLASS TUBE OUTER | Glass container | Outer cylindrical glass of the flask | Y | 1 | each | In Design | Ordered, then cut | MTS | Ali Express | 30 | 10 | $118.40 | $3.95 | $3.95
302321 | GLASS TUBE | Glass container | Inner cylindrical glass of the flask | Y | 1 | each | In Design | Ordered, then cut | MTS | Robson Scientific | 10 | 10 | $322.40 | $32.24 | $32.24
20111 | Grip | Ergonomics | Outer cover of the handle to provide user a better grip (CM-EPDM Rubber 50-A) | N | 1 | each | In Design | Injection mold | OTS | ICOMold | 10 | 15 | $338.70 | $33.87 | $33.87
4211473 | Handle | Ergonomics | Handle to allow user to better hold and move the device (ABS Chimei PA-757) | Y | 1 | each | In Design | Injection mold | OTS | ICOMold | 10 | 15 | $213.80 | $21.38 | $21.38
4504369 | 18mm countersunk M6 HEX Bolt | Fasteners | M6 18mm countersunk screw to fasten handle and grip into the chassis | Y | 8 | each | RTS |  | MTS | Singularity Supplies (Amazon) | 20 | 11 | $21.74 | $1.09 | $8.70
343500130 | Male-to-Male 10mm NPT connector | Fasteners | Male to male connector between tube plates and solenoid valve (304 Stainless Steel) | Y | 2 | each | In Design | CNC | OTS | Partzpro | 2 | 5 | $98.00 | $49.00 | $98.00
948077140 | 10mm M6 HEX Bolt | Fasteners | M6 10mm HEX bolt to secure Digestate compartment to chassis | Y | 8 | each | RTS |  | MTS | MewuDecor | 50 | 8 | $30.97 | $0.62 | $4.96
22254886 | Tube plates | Metal cover | Custom made plates for the glass tubes to be inserted into (Aluminium 6061-T6) | Y | 2 | each | In Design | CNC | OTS | Partzpro | 2 | 11 | $165.00 | $82.50 | $165.00
22043 | Pi holder | Mount | Metal mount the hold the Raspberry Pi (304 Stainless Steel) | Y | 1 | each | In Design | CNC | OTS | Partzpro | 1 | 11 | $120.00 | $120.00 | $120.00
22043 | pi screw | Fasteners | M5 screws to fasten the Raspberry Pi onto the Pi holder, and fasten holders to the chassis | Y | 10 | each | RTS |  | MTS | X-Dr | 60 | 35 | $19.32 | $0.32 | $3.22
51254683 | Bottom Shell | Plastic cover | Plastic casing to isolate the inner components from the outside, also for aesthetic purposes (ABS Cinmei PA-757) | Y | 1 | each | In Design | Injection mold | OTS | ICOMold | 10 | 15 | $585.10 | $58.51 | $58.51
922062448 | Top Shell | Plastic cover | Plastic casing to isolate the inner components from the outside, also for aesthetic purposes (ABS Cinmei PA-757) | Y | 1 | each | In Design | Injection mold | OTS | ICOMold | 10 | 15 | $585.50 | $58.55 | $58.55
921558741 | Rubber Nibs | Rubber covers | Rubber covers for the screws, providing protection to corrosion and for aesthetic purposes | N | 8 | each | RTS |  | MTS | Ozsupply | 10 | 5 | $10.00 | $1.00 | $8.00
22254862 | Valve connector | Steel fastener/tube | Stainless steel alloy threaded tube which allows the device to be attached to the tap (304 Stainless Steel) | Y | 1 | each | In Design | CNC | OTS | Partzpro | 1 | 11 | $66.00 | $66.00 | $66.00
22254851 | White LED Strips | Peripheral | LED light strips to provide lighting for camera when taking photos | Y | 0.05 | meters | RTS |  | MTS | Locinoe | 5 | 3 | $25.99 | $5.20 | $0.26
98844012 | 1kg Beam Load Cell | Peripheral | Weighing scale to measure the amount of liquid in the device | Y | 1 | each | RTS |  | MTS | core-electronics | 1 | 4 | $5.05 | $5.05 | $5.05
98843558 | SparkFun Load Cell Amplifier - HX711 | Peripheral | Amplifier that allows to read signal from load cell | Y | 1 | each | RTS | PCB | MTS | core-electronics | 1 | 4 | $19.35 | $19.35 | $19.35
2510728 | Raspberry Pi Camera Board V2 | Peripheral | High quality image sensor | Y | 2 | each | In Design |  | MTS | PiAustralia | 1 | 7 | $53.41 | $53.41 | $106.82
 |  |  |  | Total Pieces |  |  |  |  |  |  | Total Fixed |  | $3290.73 | Total | $1259.62
 |  |  |  |  |  |  |  |  |  |  | Volume |  | 100000 | Total Unit | $1259.65

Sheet: Part List
Bill of Materials (BOM)
Product Name : | AD tester device (T232's Instrument)
Assembly Name : | A1722
Author: | Ritchie Leong, Jason Ung, Xavier Andueza, Ling Chen, Kabir Chugh, John Nguyen
Assembly Revision : | 21
Approval Date : | 2022-10-07
Part ID | Category | Part Name | Description | Picture | Units | Cost
17221 | PCB | RASPBERRY PI 4 MODEL B 4GB SDRAM | Microcomputer |  | each | $88.09
17222 | Peripheral | 10mm 24V DC Solenoid Valve | 12V DC valve to control the input/output of liquids |  | each | $28.48
17223 | Metal Threaded connector | Bottom Attachment | Thread to connect waste container (Aluminium 6061-T6) |  | each | $54.00
17224 | Fasteners | Camera screw | Screws to fasten camera to the cover (ABS Cinmei PA-757) |  | each | $11.68
302201 | Mount | Camera, LED holder | Camera mount to hold the camera (304 Stainless Steel) |  | each | $193.00
302301 | Glass container | GLASS TUBE OUTER | Outer cylindrical glass of the flask |  | each | $3.95
302321 | Glass container | GLASS TUBE | Inner cylindrical glass of the flask |  | each | $32.24
20111 | Ergonomics | Grip | Outer cover of the handle to provide user a better grip (CM-EPDM Rubber 50-A) |  | each | $33.87
4211473 | Ergonomics | Handle | Handle to allow user to better hold and move the device (ABS Chimei PA-757) |  | each | $21.38
4504369 | Fasteners | 18mm countersunk M6 HEX Bolt | M6 18mm countersunk screw to fasten handle and grip into the chassis |  | each | $8.70
343500130 | Fasteners | Male-to-Male 10mm NPT connector | Male to male connector between tube plates and solenoid valve (304 Stainless Steel) |  | each | $98.00
948077140 | Fasteners | 10mm M6 HEX Bolt | M6 10mm HEX bolt to secure Digestate compartment to chassis |  | each | $4.96
22254886 | Metal cover | Tube plates | Custom made plates for the glass tubes to be inserted into (Aluminium 6061-T6) |  | each | $165.00
22043 | Mount | Pi holder | Metal mount the hold the Raspberry Pi (304 Stainless Steel) |  | each | $120.00
22043 | Fasteners | pi screw | M5 screws to fasten the Raspberry Pi onto the Pi holder, and fasten holders to the chassis |  | each | $3.22
51254683 | Plastic cover | Bottom Shell | Plastic casing to isolate the inner components from the outside, also for aesthetic purposes (ABS Cinmei PA-757) |  | each | $58.51
922062448 | Plastic cover | Top Shell | Plastic casing to isolate the inner components from the outside, also for aesthetic purposes (ABS Cinmei PA-757) |  | each | $58.55
921558741 | Rubber covers | Rubber Nibs | Rubber covers for the screws, providing protection to corrosion and for aesthetic purposes |  | each | $8.00
22254862 | Steel fastener/tube | Valve connector | Stainless steel alloy threaded tube which allows the device to be attached to the tap (304 Stainless Steel) |  | each | $66.00
22254851 | Peripheral | White LED Strips | LED light strips to provide lighting for camera when taking photos |  | meters | $0.26
98844012 | Peripheral | 1kg Beam Load Cell | weighing scale to measure the amount of liquid in the device |  | each | $5.05
98843558 | Peripheral | SparkFun Load Cell Amplifier - HX711 | amplifier that allows to read signal from load cell |  | each | $19.35
2510728 | Peripheral | Raspberry Pi Camera Board V2 | High quality image sensor |  | each | $106.82

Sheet: Revisions
Revision History
Revision | Description | Date of Approval

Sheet: Comments
Comments
Entry Date | Description | Reference (if any)
2022-10-07 | Raspberry Pi | https://www.digikey.com.au/en/products/detail/raspberry-pi/RASPBERRY-PI-4B-4GB/10258781
2022-10-07 | 10mm 24V DC Solenoid Valve | https://www.npvvalves.com.au/10mm-solenoid-coil
2022-10-07 | Bottom Attachment
2022-10-07 |  | https://www.amazon.com.au/4inch-Normally-Closed-Electric-Solenoid/dp/B085NJ824B?hvadid=463918898363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
2022-10-07 | GLASS TUBE OUTER - 80mm OD 5mm T Glass QuartZ Tubing | https://www.aliexpress.com/item/32968457150.html
2022-10-07 | GLASS TUBE INNER - 54mm OD 2.5mm T Glass tubing | https://www.robsonscientific.co.uk/quartz-glass-products/quartz-tubing?product_id=544
2022-10-07 | 18mm countersunk M6 HEX Bolt | https://www.amazon.com.au/18mm-Socket-Countersunk-Machine-Screw/dp/B07X8Q9N72
2022-10-07
2022-10-07 | 10mm M6 HEX Bolt | https://www.amazon.com.au/Button-Socket-Screws-Grade-Finish/dp/B07MG9M71X
2022-10-07 | M5 10mm philips head pi screws | https://www.amazon.com.au/X-DREE-Stainless-Crosshead-Phillips-7370209b-a222-11e9-8d7c-4cedfbbbda4e/dp/B07ZB3YJ8R
2022-10-07 | Tube plates
2022-10-07 | White LED Strips | https://www.amazon.com.au/Locinoe-Waterproof-Dimmable-Flexible-Wardrobe/dp/B09WLGZZ51
2022-10-07 | Bottom Shell
2022-10-07 | Top Shell
2022-10-07 | Grip
2022-10-07 | Handle
2022-10-07 | Camera, LED Holder
2022-10-07 | Pi holder
2022-10-07 | 1kg Beam Load Cell | https://core-electronics.com.au/makerverse-1kg-load-cell.html
2022-10-07 | SparkFun Load Cell Amplifier - HX711 | https://core-electronics.com.au/sparkfun-load-cell-amplifier-hx711-38610.html
2022-10-07 | Valve connector
2022-10-07 | Male-to-Male 10mm NPT connector
2022-10-07 | Raspberry Pi Camera Board V2 | https://raspberry.piaustralia.com.au/products/raspberry-pi-camera-board-v2
2022-10-07 | Rubber Nibs 10pc | https://ozsupply.com.au/collections/round-plastic-end-caps/products/16mm-round-plastic-end-caps-10pcs-50pcs
2022-10-07
2022-10-07
2022-10-07
2022-10-07
2022-10-07
2022-10-07
2022-10-07
2022-10-07
2022-10-07
2022-10-07
2022-10-07
2022-10-07
2022-10-07
2022-10-07
2022-10-07

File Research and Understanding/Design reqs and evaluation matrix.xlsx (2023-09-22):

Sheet: Requirements and questions
PART A
Specifications
Hard Specs | Soft Specs
Contain 100mL of digestate, maintain in the mesophylic state | Low cost
Dry weight of <10kg | Minimised weight, height, area
Height < 0.5m | Topple resistant
Base Area <0.08m^2 | Aesthetics
Rasperry Pi microcontroller with attendant electronics | Easy servicing of parts
Battery operated | Limited metal parts
Carry friendly | Ease of manufacture + assembly
No sharp corners | Schematics for electronic circuitry used
Questions
Does it need to rotate as it does in our sample kit? | We can assume that we will get good foam indication in this.
Since the process is anaerobic, am I to assume that any air entering the system is a problem?
Pressure needs to be investigated. How not to lose pressure in transfer.
It is biohazardous therefore need to follow some safety protocols. Research, take into account and document.
How do we actually get the digestate out? Is it a tap? What head does this tap have?
Submissions include:
- Drawing of the assembled device in .bmp format (as a single A4 size image).
- Detailed part and assembly CAD drawings in .dwg format (in a single zip file).
Supplementary information to be included with the drawings are (in a single word file):
(a) A parts list, where for each item the quantity, part number, description, notes/remarks is indicated;
(b) A purchase parts list, where for each item the quantity, part number, supply vendor, part/model reference, cost, notes/remarks is indicated.
(c) Justifications of how the mandatory specifications and the desirable characteristics of the system are met.
PART B
Description of efforts expended to support design features incorporated (single Microsoft word file):
- Calculations
- Simulations
- Physical experiments
- Limited to 3000 words and 10 figures

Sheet: Mechanical systems
Thoughts
- Portable, so they won't be setting down on tables out on the field. Means they need to make sure it'll scan regardless of tilt. So volume should make sure it always gets good colour.
- Needs a good grip, should be used one-handed. This is so a tap can be turned on and it will be filled up.
- Might need good seals if air will mess up the measurements?
- Should clearly be something not to be drunk from
- carry-friendly, so center of mass shouldn't be off-center.
- Should design in distinct sub-components that then all fit together. Probably bolts work fine for a lot of it? Just with a torx head or something?
- Ease of manufacture, how do plastic moulded parts usually turn out?
- Heating elements should probably be inside of the volume to make sure that the heating is consistent in the volume. May also need a top/bottom temp sensor?
- Insulation for the liquid? Would mean less power is used overall? How could this be done? How to insulate a space well, materials...
- Disposing and cleaning, would you have single use containers? Could you clean the containers? What safety hazards are there for either?
- Account for tilts in the digestate pour out process
- System should account for someone taking it out while digestate is being pulled out
- system relief valve
- Does the gas come through?
- Can talk about how there's often solids in the digestate, so the plant needs to make sure no large solids are getting through
- Foaming needs some area for gas, we need to stir to see the foam.
- Consider the tank's pressure, the liquid pressure coming through.
- pressure, temperature, humidity may effect the foaming in the handheld unit.

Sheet: Component Breakdown
Sub-Component | Key requirements
Fluid container unit | Must hold 100ml | Must have space for gas (where foam goes into) | Material can withstand acidic environment
Solenoid fluid entrance valve | Must be able to withstand expected pressures (unknown at the moment) | Withstand acidic environments
Fluid container and insulation sub-compartment | Must contain the camera, lighting too. Has spaces for required wiring to pass through
Lighting | Such that the fluid in the container is well lit from multiple sides. Will fit into the chassis | Acidic environment | Likely another solenoid? Probably can just use the same one?
Camera(s) location(s) | How many cameras is informed by testing | Where cameras are placed?
Fluid release valve | Withstand pressures
Grip | What is comfortable sizing for the average person?
Handle | What materials are comorfortable to hold? How will this attach to the grip?
Display | What is a good sized display? This should account for potentially being the "wrong" direction
Electricals | Make sure all key electricals are in
Chassis | How does everything now slot together? Make sure that all parts and the chassis have bolt holes that make sense
Electricals holder | Where are all electricals kept? Will they need some sort of ventilation?
througputs | Make holes in the part for required wiring/cabling

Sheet: Calculations
Glass Cylinder ID (mm) | Area (mm^2) | Required height (assuming 200mm^3)
10 | 78.53981634 | 2546.479089 | Glass tube thickness: | https://pegasus-glass.com/Home/Products/GlassTubingandGlassRod/GlassTubing/StandardGlassTubing/StandardTubing10mm127mm/tabid/253/Default.aspx
15 | 176.7145868 | 1131.768484 | Inner | 60mm diameter, 5mm thickness
20 | 314.1592654 | 636.6197724 | Outer
25 | 490.8738521 | 407.4366543
30 | 706.8583471 | 282.9421211
35 | 962.1127502 | 207.875844
40 | 1256.637061 | 159.1549431
45 | 1590.431281 | 125.7520538
50 | 1963.495408 | 101.8591636
60 | 2827.433388 | 70.73553026
Volume required: | 200000
49 | 1885.74099 | 106.0591041

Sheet: References
Solenoid Valve: | https://grabcad.com/library/wicvalve-solenoid-1-8-1/details?folder_id=11658118

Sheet: To-do
Priority | Description | Difficulty | Ideas | Progress
1 | Plastic container cannot actually be assembled as it is. |  | Break into two components that you clip into eachother | DONE
2 | Handle - the container needs a grip |  | Have a grip that you attach to the case, screw into the plastic. Plastic needs a flat base for these.
3 | Top connection to valves |  | Standard thread up top, this would then be modular depending on what types of heads they have (we sell connectors separately to order)
4 | Bearings on top, servo down bottom to spin the fluid around |  | Likely infeasible. Should chat to group on this
5 | Installation of electronics | Difficult. Requires its own page probably | Can have most of the electronics in the bottom or the top sections
6 | Default attachment for the waste bags | Moderate, requires some bottom modifications | screw up into the plastic/metal?
7 | On/Off buttons
8
9 | Need to actually place a joiner between the solenoid and the metal top and bottom of the glass tube. |  | Can use one of the double-headed joiners I've previously used before at Agilent
10 | Grip bolts could be sunken
11
12
13
14
15
16
17
18
19
20
21
22

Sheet: Electricals
Electrical components required | CAD Model Sourced? | Expected location | Sub-components | Notes | Links
Raspberry Pi |  | Down bottom | Wires leading to the other components | In and attached. No cables uet | Grabcad: https://grabcad.com/library/raspberry-pi-3-model-b-reference-design-solidworks-cad-raspberry-pi-raspberrypi-rpi-1
Battery | Can't find, should make a simple one | Down the bottom | Standard PC cable for charging Wires to the raspberry pi
Camera | Y | In central compartment | Wires, holder for camera | In and attached No cables yet | Grabcad: https://grabcad.com/library/raspberry-pi-camera-4
Lights | Y | In central compartment, next to camera is better | Wires, holder. | Could do a powered White LED Strip? No cables yet
Load cell |  | Between the metal and the plastic |  |  | https://grabcad.com/library/low-profile-compression-load-cell-1kn-ultra-thin-weight-sensor-100kg-1
 |  |  |  |  | https://core-electronics.com.au/sparkfun-load-cell-amplifier-hx711-38610.html
 |  |  |  |  | https://core-electronics.com.au/makerverse-1kg-load-cell.html
Valves | Y | In sub-compartments | Wires, connectors | No cables yet. | https://au.element14.com/delta/dsos-0416-05d/linear-solenoid-5vdc-3-3w/dp/3533173?mckv=_dc|pcrid||pkw||pmt||slid||product|3533173|pgrid||ptaid||&CMP=KNC-GAU-GEN-SHOPPING-PLA-PMAX
Other Notes
When it comes to buildability, we need to make sure that the wiring is all completed before the top and bottom are connected bottom etc. is all put in.
Wiring should never be in front of the camera
Other components I need to think on
- Lights, their wiring (also only on when the fluid is filled?)
- Batteries. Need to power the raspberry pi and also the heating unit

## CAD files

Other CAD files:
Solidworks files/DESIGN - Final/Raspberry Pi/Raspberry pi 3 cam V2,1/Cam V2.1 v1.step
Solidworks files/DESIGN - Final/Raspberry Pi/Rpi components/HANRUN2_HR911105A.sldprt
Solidworks files/DESIGN - Final/Raspberry Pi/Rpi components/Strait Headers.SLDPRT
Solidworks files/DESIGN/Raspberry Pi/Raspberry pi 3 cam V2,1/Cam V2.1 v1.step
Solidworks files/DESIGN/Raspberry Pi/Rpi components/HANRUN2_HR911105A.sldprt
Solidworks files/DESIGN/Raspberry Pi/Rpi components/Strait Headers.SLDPRT

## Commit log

2023-09-22 implemented servo
2023-09-22 design files
    [Design reqs and evaluation matrix.xlsx, Team232 - Bill of Materials version 1.xlsx, Team232 - Bill of Materials version 2.xlsx, Team232 - Bill of Materials ver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]
2023-09-22 solidworks files
    [10mm M6 HEX Bolt.SLDPRT, 10mm Solenoid Valve.SLDPRT, 18mm countersunk M6 HEX Bolt.SLDPRT, Blown Out Assembly Electricals.SLDASM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]
